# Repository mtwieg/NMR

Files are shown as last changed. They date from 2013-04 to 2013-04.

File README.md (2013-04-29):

NMR
===

Welcome to the Open Source Mobile NMR Relaxometry Platform repository on github.

You can download the entire repository without needing to install or register with github. To do so, go to the repository homepage and click the ZIP icon on the upper toolbar.

After presenting this project at ISMRM 2013, I received several questions about the future direction for the platform. At the moment there are numerous possible improvements to the hardware:

1. Further minitiarization (we estimate the platform could be shrunk by a factor of three or so without compromise).

2. Wider frequency range (for very low field work)

3. Addition of gradient amplifiers (imaging)

4. Greater processing power, for standalone data processing.

Such improvements should be driven by the intended applications of the platform, and at this time we have not settled on any applications to explore.  Until we decide what sort of applications are worth pursuing, we will probably hold off on any major hardware revisions.

We are, of course, open to any and all suggestions.

Mike Twieg
mdt24@case.edu

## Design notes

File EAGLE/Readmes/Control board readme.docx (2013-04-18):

Control board notes

The control board conditions the main DC supply voltage into the various supply rails for the rest of the platform. The main power input port is protected against reverse voltage polarity. There is also a resettable fuse and a clamp to protect against overvoltage (18V nominal) and prolonged overcurrent conditions. Operating the platform with supply voltages outside the nominal range (12-18VDC) will require modifications to the power chain.

The control board circuitry provides the option of shutting off different parts of the power supply chain to mitigate interference during signal acquisition. As of now, this feature has not been implemented, either in hardware or in firmware.

The control board has a 10 pin JTAG header which is used to program the MCU. For our purposes we used the JTAG ICE-3 programmer from Atmel in order to program and debug the platform firmware.

Some notes on uSD cards: Standard SD cards can operate in two modes: SD mode and SPI mode. Most electronic devices use SD mode; however, this requires a specialized peripheral interface from the host system, which was not available on our selection of MCU. Therefore we used SPI mode, which uses a simple SPI port found on most MCUs, including ours.

One implication of using the SD card in SPI mode is that the listed specifications for a given SD card are valid only for SD mode, and therefore performance in SPI mode is not guaranteed. We have discovered that in SPI mode, different card models and manufactures give vastly different performance results, independent of the label specifications. Certain SD card model (such as the SDSDQY-004G-A11A from SanDisk) performed quite well using SPI mode and our custom SD card firmware, and therefore we recommend using this model.

Michael Twieg

mdt24@case.edu

March 2013

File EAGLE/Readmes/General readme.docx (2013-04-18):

General schematic/layout

The circuit schematics and layouts were designed using Eagle Cad Professional. The free (hobbyist) version of Eagle should be able to display all included files, though editing them may not be possible without the Professional version.

The included BOMs cover all components except for basic, general purpose surface mount resistors and capacitors. Unless otherwise noted on the schematic, all resistors are 1% tolerance. General nonpolarized capacitors can be assumed to be NP0 dielectric for values of 1nF or less, and X7R dielectric for values over 1nF. All capacitors in case size 1008 are low loss NP0 types.

For professional PCB fabrication, we recommend either EIconnect or Advanced Circuits.

Michael Twieg

mdt24@case.edu

March 2013

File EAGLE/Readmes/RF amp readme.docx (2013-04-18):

Notes on the TRSW/RF amp circuitry

It has been observed that excessive RF power on the LNA input can lead to failure of the LNA. Adequate isolation on the RXSW is necessary to prevent this. See section 2-3 of the thesis for guidance on selecting Vr.

The gain control voltage of both VGAs can be set with potentiometers. The second stage VGA may also be set using the DAC from the MCU. When using the DAC for gain control, do not populate the potentiometer circuitry for the second stage VGA.

Michael Twieg

mdt24@case.edu

March 2013

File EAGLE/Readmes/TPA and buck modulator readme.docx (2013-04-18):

TPA and buck modulator notes

The buck modulator has the capability to deactivate its operation with the SHDN pin header. This feature has not been implemented yet, in either the firmware or hardware, as it was not deemed necessary.

Many component values in this design are specific to this TPA CMCD tuning (8.35MHz with a 1:4 balun). If the CMCD circuit is altered, changes to the buck modulator may also be necessary to preserve stability.

The LM5113 gate driver has shown to be useful at RF frequencies up to 20MHz. If higher frequency gate drive is desired, then it may be necessary to use a different gate drive circuit based on narrowband impedance matching circuits.

The tuning capacitors (C104 and C106) and the tank inductor (L1) for the CMCD were adjusted empirically to give good efficiency at the desired frequency. As a rule of thumb, the characteristic impedance of the resonant tank should be less than or equal to the load impedance looking into the balun.

Michael Twieg

mdt24@case.edu

March 2013

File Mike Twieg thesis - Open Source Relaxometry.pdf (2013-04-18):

OPEN SOURCE NMR RELAXOMETRY PLATFORM

by

MICHAEL TWIEG

Submitted in partial fulfillment of the requirements

For the degree of Master of Science

Thesis Adviser: Dr. Mark Griswold

Department of Electrical Engineering and Computer Science

CASE WESTERN RESERVE UNIVERSITY

January 2013

CASE WESTERN RESERVE UNIVERSITY

SCHOOL OF GRADUATE STUDIES

We hereby approve the thesis/dissertation of

Michael Twieg

Master of Science
candidate for the ________________________________degree *.

Mark Griswold
(signed)_______________________________________________ (chair of the committee)

Kenneth Loparo
________________________________________________

Francis Merat
________________________________________________

________________________________________________

________________________________________________

________________________________________________

July 23, 2012
(date) _______________________

*We also certify that written approval has been obtained for any proprietary material contained therein.

i

Table of Contents

ii

4-4: Example application: Measurement of G0 by diffusion weighted experiment.......98

4-5: Example application: Spoiling of milk | 100
4-6: Example application: Curing of adhesives | 102
4-7: Example application: Surface probe for biosensor applications | 107
Chapter 5: Conclusions and future directions | 109
Appendix A: Selected experiment parameters | 111
Appendix B: Circuit schematics | 120
Bibliography | 129

iii

List of tables

No tables

No tables

Table 4-4-1: Results of self diffusion coefficient measurement for three samples.....100

Table 4-7-1: Changing sensitivity and noise for the surface probe under different

iv

List of figures

Figure 1-3-2: Distortion of the FID due to B0 inhomogeneity results in an effective T2*

Figure 2-1-1: Schematic cross sectional diagram of our custom single sided magnet

Figure 2-1-5: a) Fit G0 vs. y using fitting window of 6mm b) Fit G0 vs. B0 using fitting

Figure 2-2-1: Cross sectional diagram of the magnet and harness with a flat surface coil

Figure 2-2-3: Cross sectional diagram of the magnet and harness with solenoid volume

Figure 2-2-5: Oscilloscope captures of the TXSW signal (channel 1, yellow) and the

Figure 2-3-2: Isolation between TX and RX ports when RXSW is on and TXSW is off

Figure 2-3-3: Isolation between TX and RX ports when RXSW is off and TXSW is on

Figure 2-3-4: Maximum permissible RF power isolated by the TRSW for two example

Figure 2-3-5: Attenuation from TX to Coil port when TXSW is on, RXSW is off.......39

v

Figure 2-3-6: Attenuation from Coil to RX port when TXSW is off, RXSW is on ......39

Figure 2-4-3: Spectral content of the 8.35MHz TPA output at full power (VD=12V),

Figure 2-4-4: Plots of drain efficiency and power added efficiency (PAE) vs.

Figure 2-5-2: Small signal step response of buck modulator between 6V and 8V........47

Figure 2-5-3: Large signal step response of buck modulator between 1V and 10V......47

Figure 2-6-2: Gain of the RF amplifier chain, with maximum gain for both AD8331

Figure 2-7-1: Frequency mixing of a real passband signal at f0 with a LO carrier........55

Figure 2-7-2: Simplified diagram of the downconversion stage, baseband amplifiers,

Figure 2-8-3: Block diagram of the power supply conditioning on the control board...64

Figure 3-1-1: CPMG readout sequence diagram, showing decay in spin echo amplitude

vi

Figure 3-1-5: Constant relaxation preparation sequence, with start of CPMG readout.74

Figure 3-1-6: Elimination of ringing artifacts from one spin echo via phase cycling ...75

Figure 3-2-1: Detailed operation of the platform I/O for synthesizing a RF pulse and
sampling a spin echo during a CPMG | 79
Figure 3-3-1: Hierarchy of the experiment structure | 82
Chapter 4: Hardware verification results | 89

Figure 4-1-1: a) Acquired data from a single spin echo. b) DFT magnitude of the
acquired echo, after zero padding to N=100 | 90

Figure 4-1-2: a) Acquired data from a single spin echo. b) Complex DFT of the
acquired echo, after zero padding to N=100 | 91

Figure 4-2-1: Results of flip angle calibration experiment for pulse width=10 μs and
pulse width=20 μs | 94

Figure 4-3-1: a) Measured echo amplitude for the above CPMG sequence. b)
exponential fit and error signal of the CPMG echoes | 97

Figure 4-4-1: a) Constant relaxation diffusion experiment results for a) DI water, b)
acetone, and c) glycerol | 99

Figure 4-5-1: Plots of experimental results for the fat free and whole milk samples
with different room-temperature storage times | 101
Figure 4-6-1: Photo of experimental setup for measuring curing of adhesives | 103

Figure 4-6-2: Plots of a) initial magnetization and b) apparent T2 for JBweld epoxy .104

Figure 4-6-3: Plots of a) initial magnetization and b) apparent T2 for exposed Duco
Cement | 105

Figure 4-6-4: Plots of a) initial magnetization and b) apparent T2 for Duco Cement in
between two fiberglass layers | 106
Chapter 5: Conclusions and future directions | 109

No figures

vii

Acknowledgements

First and foremost, I wish to give thanks to my research advisor Dr. Mark Griswold for his support and guidance throughout this project. Mark graciously introduced me into the incredible field of NMR/MRI, and gave me the opportunity to conduct research in one of the best imaging research groups in the country.

I am also indebted to Dr. Ken Loparo and Dr. Frank Merat for taking their own time to participate in my committee and review this work.

I also extend my warmest gratitude to the following:

To my many colleagues in the Case Center for Imaging Research, who provided me with support and advice on the theory and practice of NMR on countless occasions, and who shared their experiences and wisdom for my own benefit. They are Matt Riffe, Natalia Gudino, Lisa Bauer, Katie Wright, Dan Ma, Anagha Deshmane, Eric Pierre, Yun Jiang, Nahal Geshnizjani, Nicole Seiberlich, Greg Lee, and Vikas Gulani.

To Colin Blumenthal, the most diligent and reliable summer assistant I could possibly ask for.

To Carol Rice, for her swift handling of countless material requisitions.

To Cena Myers Hilliard, for her assistance in navigating the bureaucracy between our two departments.

To Joe Molter, for his assistance in the use of our 3D printer was invaluable throughout this project.

To Dr. James Basilion and Dr. Richard Agnes, for allowing me access to their lab equipment and materials on numerous occasions.

To Ed Burwell, George Daher, and Larry Sears, for affording me the incredible guidance and materials that turned me to electrical engineering.

To Beth Murray, for years of advice and tiny candies in EECS.

To Ian Charnas and the staff of the Thinkbox, for the use of various Thinkbox resources.

And last, but of course not least, to my parents Robert and Deborah for their unconditional love and support throughout my academic career.

viii

Open Source NMR Relaxometry Platform

Abstract

by

MICHAEL TWIEG

We present a low cost, open source hardware platform for use in NMR

relaxometry experiments. The platform is capable of a wide variety of relaxometry

experiments comprising many magnet, coil, and sample combinations. The majority of

the RF chain is broadband, allowing operation over a large frequency range with only

minor adjustments to the hardware. Experiments can be performed in a host-controlled

mode in conjunction with a PC, or in a standalone mode for mobile applications. The

high degree of flexibility and low cost of the platform makes NMR relaxometry

accessible to applications where cost, size, or flexibility were previously prohibitive. The

system is based on off-the-shelf components, along with some custom-fabricated parts,

and can be replicated by engineers with suitable skills and resources. The design of the

platform is open source.

Chapter 1: NMR relaxometry theory and applications

1-1 Content overview

Chapter one introduces the field of NMR relaxometry and its application. The

basic principles of NMR physics will be introduced, including magnetization, precession,

relaxation, and spin echoes. The Bloch equations and the effects of self diffusion will also

be derived. The influence of static field inhomogeneity and its impact on NMR

relaxometry will also be addressed. Finally, the field of NMR relaxometry and some of

its various applications will be discussed.

Chapter two describes the general hardware aspects of NMR systems. A

generalized NMR system will be divided into its basic components, and their roles within

the NMR system are discussed separately. We will show how the specifications for each

component are determined according to the specific requirements and limitations of the

application, and how we implement our hardware according to these specifications.

Finally, we will evaluate the performance of each component and its impact on the

overall system performance.

Chapter three covers the theory and implementation of NMR relaxometry

experiments on our platform. First we will discuss various pulse sequences and how they

can be used to obtain contrast according to various relaxation mechanisms. Secondly we

will explain how pulses are synthesized and how NMR signals are sampled with the

actual platform hardware, and how these events are combined into the desired sequences.

Thirdly, we will explore how the sequences are executed by the platform firmware, and

how sequences and experiments are defined within the firmware. Finally, we will discuss the user interfaces featured in the platform, and how data is stored and transferred within

the platform and between the platform and host.

Chapter four discusses the analysis of the overall platform performance and

experimental results. First we will discuss how sampled data from the platform is

analyzed using Fourier transforms and curve fitting algorithms. Secondly, we will explain

how sequence parameters can be calibrated for best performance. Thirdly, we compare

empirical measurements of signal to noise ratio and flip angle calibration with theoretical

predictions. Finally, we will demonstrate several examples of relaxometry experiments

and discuss their results.

Chapter five will provide an overview of the platform's specifications and

applications. Potential improvements to the platform hardware will be discussed. Finally,

we will speculate on future applications for the platform in research.

1-2 Introduction

Since its discovery, nuclear magnetic resonance (NMR) has shown to be an

excellent method of observing the nature and behavior of matter on the molecular scale.

While NMR was at first studied only within the fields of physics and chemistry, it has

since spread to a wide variety of disciplines and industries. Currently the most well

known application of NMR is medical magnetic resonance imaging (MRI), but it has also

found applications such as the investigation of molecular structures, porous media,

quality control for food products, inspection of polymer quality, and many more [2–10].

NMR is a particularly powerful tool because, given the correct magnet and coil

configuration, it can non-invasively penetrate into objects and provide spatial maps of many different material properties (which is the basis of MRI). Despite its power of

insight, it does not require any chemical reactions to occur and does not use any ionizing

radiation, and is thus a completely nondestructive method.

Arguably NMR's greatest weakness is the cost and complexity associated with the

various hardware components required to perform many studies. However, many simple

studies, especially those that do not require imaging, have much simpler requirements

that can be satisfied at lower cost. One subset of NMR studies with such low

requirements is NMR relaxometry. Despite its relative simplicity, NMR relaxometry can

provide valuable insight into many physical and chemical processes and structures.

The main motivation for the development of our relaxometry platform was to

make NMR relaxometry more accessible to researchers by lowering the cost and

complexity of the hardware, while still offering high performance and flexibility. The

platform allows for a wide variety of applications with various field strengths, magnet

and coil geometries, and samples. A secondary goal was to construct a system that was

small and portable, such that it could even be worn. As designed, the platform can be

used with its own battery, and it is small and light enough for mobile applications. The

platform is compatible with a large variety of different magnet and coil designers,

customized for the relaxometry application. However, the main magnet for such a system

is typically highly inhomogeneous, and requires specialized acquisition techniques to

ensure that the required signals are received with high sensitivity.

1-3 Fundamentals of NMR physics

Sample magnetization

The basis of NMR is that atomic particles possess a net spin, characterized by the

spin quantum number (s in the context of electrons, I in the context of nucleons). The

spin quantum number is quantized, and has allowed values of positive integers and half

integers. We will restrict our discussion to protons (in the form of hydrogen 1H), and

therefore use I as the spin quantum number, which has a value of ½. The secondary spin

quantum number mI describes the magnitude and direction of the angular momentum of

the nuclear spin, and can have values from –I to +I in integer steps. The spin of the

particle gives rise to a magnetic moment μ, which is given by:

- mI µ = γ
Equation 1-3-1

Where γ is the gyromagnetic ratio of the nucleus (

γ = 267.5rad s

for 1H) and ℏ is the

reduced Planck’s constant. For nuclei with no orbital angular momentum (such as 1H),

this can also be written as:

µ = γ I

Equation 1-3-2

Where

I
is the spin angular momentum vector. In the absence of an external magnetic

field, the different spin states described by mI are degenerate, meaning that all states

occupy the same energy level. At thermal equilibrium the members of a population of

nuclei will have their states evenly distributed, and the net mI
, and the net magnetization

of the population, will be zero [11].

If an external, static magnetic field

B0
is introduced to the population of nuclei,

the different states mI will no longer have the same energy level, and thus the population of spins will be biased parallel to

B0
. The spins will effectively polarize themselves to

align with

B0
, giving rise to a net equilibrium magnetization

M 0
[12]:

( )
kT
B M | N | I I
3

1

0

2 2
0
= γ +
Equation 1-3-3

Where N is the number of spins per unit volume, I is the nuclear spin quantum number

(I=
2

1
for 1H), k is Boltzmann's constant, and T is temperature.

The coordinate system describing a NMR experiment is typically defined such

that

B0
is aligned with the
z

ˆ
direction. Therefore from here on the static field

B0
will be

referred to simply as B0, and it will be assumed that it is in the z

ˆ
direction.

Larmor precession

When a macroscopic magnetization exists, the basic theory of nuclear precession

can be adequately described with classical, rather than quantum mechanics. A magnetic

moment
µ

will experience a torque

Γ
in the presence of an external magnetic field B

:

Γ = µ ×B
Equation 1-3-4

The torque results in a change in the angular momentum vector I

ˆ
:

= Γ
dt

d I
Equation 1-3-5

Combining equations 1-3-2, 1-3-4, and 1-3-5 yields the following:

B
dt

d
= γ µ ×

µ
Equation 1-3-6

Equation 1-3-6 states that when a nuclear moment µ

and

B
are not aligned,
µ

will rotate

around

B
with a frequency equal to ω [11]:

ω = γB
Equation 1-3-7

This phenomenon is called precession, and ω is known as the precession angular

frequency. We may rewrite equation 1-3-6 by splitting
µ

and

B
into their longitudinal

and complex transverse components:

z z µ = µ ·

ˆ

Equation 1-3-8

(x iy) xy µ = µ ·
ˆ
+

ˆ

Equation 1-3-9

B B z z
= ·

ˆ

Equation 1-3-10

B B (x iy) xy
= ·

ˆ
+

ˆ

Equation 1-3-11

( )

## [ (t)B (t) (t)B (t)]

i
dt
d | t
xy | xy | xy | xy

z

* | *
2
µ | µ
µ | γ
= | - | Equation 1-3-12

( )

## i [ (t)B (t) (t)B (t)]

dt

d | t
xy | z | z | xy
xy | γ µ | µ

µ
= - | - | Equation 1-3-13

If we consider the case where

B
is static with magnitude B0 and is aligned with the z

ˆ

direction, we find that equations 1-3-12 and 1-3-13 reduce to:

( )
= 0
dt

d t µ z
Equation 1-3-14

( )
( )B0
i t
dt

d t

xy

xy | γµ

µ
= - | Equation 1-3-15

Which have the solutions:

( ) | (0) z | z µ t = µ
Equation 1-3-16
( ) | | ( )
i | t
xy | xy t | e
0 0

ω
µ µ
=
Equation 1-3-17

Where

0 B0 ω = γ
is the Larmor precession frequency [11].

These equations are valid in the laboratory reference frame, which is stationary.

However, a more convenient way of describing NMR magnetization is with the rotating reference frame, in which the coordinate system rotates in the transverse plane at an

angular frequency Ω, which is normally set to be equal to ω0. Coordinates and variables

in the rotating reference frame are denoted with ' (for example
x

ˆ′ , B1

′ , µ xy
′
, etc). For the

case where Ω= ω0, equations 1-3-12 and 1-3-13 become:

( )

## [ (t)B (t) (t)B (t)]

i
dt
d | t
xy | xy | xy | xy
z | =
′ | ′ | - ′ | ′
| * | *
2
µ | | µ
µ | γ
Equation 1-3-18

( )
i (t)B (t)
dt
d | t
z | xy
xy | =
′

′
γµ

µ
Equation 1-3-19

And for our case of simple Larmor precession, equations 1-3-16 and 1-3-17 reduce to:

( ) | (0) z | z µ t = µ
Equation 1-3-20
( ) | (0) xy | xy µ′ t = µ′
Equation 1-3-21

We can see that the Larmor precession component of the transverse magnetization has

disappeared from the equations [11]. The transverse magnetization is still precessing in

the laboratory frame, but is stationary in the rotating reference frame.

Excitation via an RF magnetic field

Now we will consider the case where, in addition to the static field B0, we

introduce a circularly polarized magnetic field in the transverse plane with magnitude B1.

( )
i | t
xy B t | | B e
0
| | 1
- ω
=
Equation 1-3-22

When expressed in the rotating reference frame, B1 is constant and points in the x

ˆ′

direction:

( ) B1 B t
xy

′
=
Equation 1-3-23

The differential equations 1-3-18 and 1-3-19 then become:

( ) | B [ (t) | (t)]
i
dt
d | t
xy | xy

z

*
1 2
µ | µ
µ | γ
=

′ - ′
Equation 1-3-24
( ) | B1 dt
d | t

y

z | γµ

µ
=

′
Equation 1-3-25

( )
( )B1
i t
dt

d t

z

xy | γµ

µ
=

′
Equation 1-3-26

We can see that these equations describe rotation of the magnetization around the x

ˆ′

direction in the rotating frame. The rate of this precession ω1 is given by

1 B1 ω = γ
[11].

This precession describes how RF fields are able to manipulate magnetization, for

example by tipping it from the longitudinal axis
z

ˆ
into the transverse plane. RF fields are

needed to perturb the equilibrium longitudinal magnetization into the transverse plane in

order for precession to be detected.

An RF pulse is primarily characterized by its flip angle, which describes the

overall rotation of
µ

about

B1

. For example, a RF pulse with a flip angle of 90° may

rotate longitudinal magnetization completely into the transverse plane, and a 180° pulse

may invert longitudinal magnetization into the - z

ˆ
direction.

NMR relaxation and the Bloch equations

The previous equations describing Larmor precession are valid for an idealized

magnetic moment
µ

. However, in real NMR experiments we consider the overall

magnetization

M
from a sample, which is composed of the contributions of many spins

each with their own
µ

[11]. Large populations of spins undergo relaxation processes that

do not occur for isolated spins.

Longitudinal relaxation, also called spin-lattice relaxation or T1 relaxation, is the

process by which the longitudinal component of
M
approaches its thermal equilibrium value M0 (see equation 1-3-3). Longitudinal magnetization obeys the following linear

differential equation:
( ) | ( )

1

0
T

M M t
dt
dM t | z z
=
Equation 1-3-27

So longitudinal relaxation takes the form of an exponential decay towards M0 with a time

constant equal to T1 [11].

Transverse relaxation, also called spin-spin relaxation or T2 relaxation, is the

process by which the transverse component of
M
approaches zero. Transverse relaxation

obeys the following linear differential equation:
( ) | ( )

T2

M t
dt
dMxy t | - | xy
=
Equation 1-3-28

So transverse relaxation takes the form of an exponential decay towards zero with a time

constant equal to T2 [11].

Relaxation can be integrated into the previous equations in the following way:

( )
[ ( ) ( ) | | ( ) ( )]

( )

1

* | * | 0
2 | T
M | M t
M t B t | M t B t

i
dt
dM t | z
xy | xy | xy | xy

z

=
′ | ′ | - | ′ | ′ | +

γ
Equation 1-3-29

( )
( ) ( )

( )

T2

M t
i M t B t
dt
d | t | xy
z | xy

xy

′
=

′ -

′
γ

µ
Equation 1-3-30

These are the fundamental Bloch equations in the rotating reference frame, simplified for

on-resonance magnetization. Equation 1-3-31 below shows the correct equation for

M xy

′

when off resonance is considered:

( )
( ) ( ) | ( )

( )

T2

M t
i M t B t | i | M t
dt
dM t | xy
z | xy | xy

xy

′
=
′ | - Δ | ′ | -

′
γ | ω
Equation 1-3-31

Where Δω is the off resonance frequency [11].

The earliest NMR experiments were performed with continuous RF excitation,

while continuous absorption [13] or emission [14] of energy due to Larmor precession

was observed. Later on, experiments used pulsed RF to quickly tip, or excite, longitudinal

magnetization into the transverse plane, and it was found that precession persisted long

after the end of the RF pulse itself. The precession which persists after an excitation pulse

is referred to as free induction decay, or FID [15].

Suppose that the static field B0 is perfectly homogeneous (Δω and ΔBz are zero),

and that the sample magnetization has reached its thermal equilibrium (

M | M z ˆ
0 = | ·
). If

we apply a 90° excitation, then all of Mz will be tipped into the transverse plane where it

precesses as a FID. The FID will decay according to T2, and Mz will relax from zero back

towards M0 according to T1.

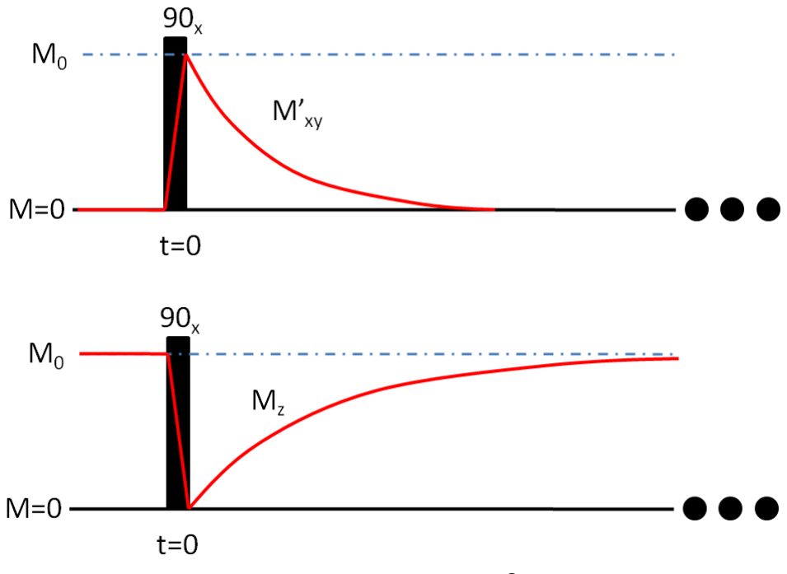
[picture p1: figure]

Figure 1-3-1) Diagrams of a simple FID experiment. At

t < 0
, Mz has reached the thermal equilibrium value M0, and Mxy is 0. At

t = 0
, a 90° RF pulse in the

x

ˆ′
direction tips all of Mz

into M'xy. a) shows the
decay of M'xy (solid red line) according to T2 b) shows the regrowth of Mz (solid red line) towards M0 (dashed blue line) according to T1.

Transverse relaxation and longitudinal relaxation are relevant because they provide a

macroscopic fingerprint of microscopic phenomenon in the environment of the spins. The

exact mechanisms of this relaxation are beyond the scope of this work, but there are countless examples of prior studies that confirm that NMR relaxation can provide key

insight into the environment of a material at a molecular scale.

B0 inhomogeneity and T2*

In the case where the static field is not perfectly homogeneous within the volume

of a sample under test (SUT), the macroscopic behavior of the transverse magnetization

will differ from the ideal FID. This is because any field inhomogeneity will result in a

frequency inhomogeneity, which will contribute to dephasing of the spins within the

SUT. This results in an apparent change to the shape of the overall FID. The exact shape

of the FID will depend on the exact nature of the inhomogeneity, but the overall result is

that the FID will decay at a rate faster than its spin-spin relaxation rate T2. The new

inhomogeneity-weighted decay time constant is referred to as T2* (even though this does

not necessarily obey a purely exponential decay [11]).

Figure 1-3-2) Distortion of the FID due to B0 inhomogeneity results in an effective T2* which is less than T2. The shape of this FID will depend on the specific nature of the inhomogeneity, and may not be exponential. The dashed red line shows a hypothetical FID in a homogeneous field, while the solid red line shows the FID in the presence of field inhomogeneity.

In many cases, inhomogeneity is so severe that T2* is far less than T2, making

observation of T2 impossible from a simple FID experiment. In such cases, spin echoes

must be used to rephase the magnetization.

Spin echoes

The Hahn echo (sometimes referred to simply as a spin echo) is a technique used

to observe the FID in the presence of B0 inhomogeneities, and was originally described

by Erwin Hahn [16]. In a simple Hahn echo experiment, an excitation pulse in the
x

ˆ′

direction occurring at
t = 0

tips some or all of Mz into the transverse plane (initially in

the
y

ˆ′
direction). The transverse magnetization is allowed to precess and decay according

to T2*. At some time
t =τ

, there is another RF pulse with a tip angle of 180° (again in

the
x

ˆ′
direction), called a refocusing pulse. The refocusing pulse rotates the magnetic

moment
µ

of each spin around the
x

′
axis, such that their transverse moments become:
( ) | ( )
+ | -
µ′ τ = µ′ τ
| *
xy | xy

Equation 1-3-32

This can also be viewed as a phase reversal of each spin:
( ) | ( )
+ | -
θ τ = -θ τ
Equation 1-3-33

After the refocusing pulse, each spin will continue to precess at its own off resonant

frequency and in the same direction, but now instead of the phase of each spin continuing

to diverge from zero, it will converge towards zero at the same rate. The result is that at

time
t = 2τ

, the phase of all spins will again be zero, and they will be coherent until they

again dephase. Aside from the Hahn echo, there are various other spin echo types that

rephase magnetization in their own way. However for the scope of this work, only Hahn

echoes will be considered.

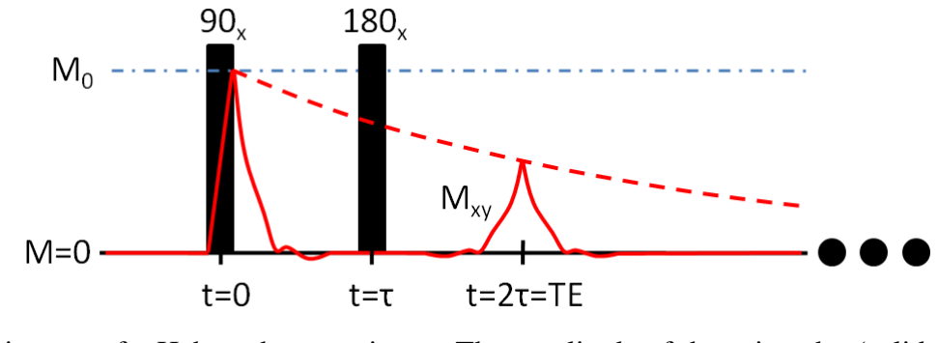
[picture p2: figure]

Figure 1-3-3) Diagram of a Hahn echo experiment. The amplitude of the spin echo (solid red line) at t=TE will be the same as the amplitude of the ideal FID without inhomogeneity (dashed red line).

Though the spin echo restores coherency in the spins at time
t = 2τ

(also called

the echo time TE), transverse relaxation still occurs due to spin-spin relaxation during

that time, and that loss in transverse magnetization cannot be restored by the refocusing

pulse (because it is due to random processes which cannot be reversed). Thus the peak

amplitude of the spin echo will still be weighted by T2 decay. This allows T2 weighted

experiments to be performed even in the presence of strong inhomogeneity in B0.

Self-diffusion

In a spin echo experiment performed in an inhomogeneous field, the amplitude of

the spin echo at the echo time TE will be equal to the initial magnetization, attenuated by

T2 relaxation. This is the case when the Larmor precession frequency (and therefore Δω)

of each spin remains constant throughout the experiment. If this is not the case, either due

to motion of the nuclei or changes in ΔB0 during the experiment, the time of the echo

coherence, or the amplitude of the echo, may be altered. One particularly relevant

example of this is molecular self-diffusion.

Self-diffusion is the phenomenon that describes the Brownian motion of particles

in a medium when the overall chemical gradient is equal to zero. The self-diffusion

coefficient D of some particles in a medium describes the mean square spatial deviation

2
δ
of the spins per unit time
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
Equation 1-3-34

Suppose the strength of our static field B0 is not constant over space, and instead varies

linearly in one arbitrary direction
g

ˆ
such that its
z

ˆ
component Bz as a function of

position
r
is given by:

Bz

## (r) Bz

(0) G r g
ˆ
0 = | + | ·
Equation 1-3-35

This is commonly referred to as a field gradient, where G0 is called the gradient strength,

in Teslas per meter. It can be found that if a population of spins is allowed to self diffuse

with D in a linear gradient G0 for time t, the spins will evolve with a random distribution

of phase [11]:

2 2 3
0

2 3
ˆ

2 2
2 | 0
3

2
3
G | Dt
G | t

d

r
γ
τ

γ δ
φ = | =

Equation 1-3-36

This dephasing causes a loss in overall transverse magnetization (ignoring the effects of

T2) according to [11]:

( ) ( )
2

2
0

φ
M | t = M | e xy | xy

Equation 1-3-37

( ) ( )

G t D
xy | xy M t | M | e

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
Equation 1-3-38

This decay is often much faster than T2 decay, especially in viscous liquids and strong

gradients. However, the effect of self-diffusion on the magnetization can be mitigated

through the use of spin echoes. Consider a simple Hahn echo experiment as described

previously. During the interval

0 < t <τ , the magnetization will relax according to

equation 1-3-38 above. At

t =τ
:

15 ( ) | ( )
G | D
xy | xy M | M | e

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
Equation 1-3-39

At
t =τ

the refocusing pulse reverses the phase of each spin. Starting from

+
t =τ
, the

magnetization continues to dephase from

( )
+
τ M xy
according to equation 1-3-38, and at

t = 2τ

, a spin echo will occur with:

( ) | ( )
G | D
xy | xy M | M | e

2 3
0

2
3

1
2
γ | τ
τ | τ
- +
=
Equation 1-3-40

Substituting equation 1-3-39 into equation 1-3-40 yields:

( ) | ( )
G | D
xy | xy M | M | e

2 3
0

2
3

2
2 | 0
γ | τ
τ
=
Equation 1-3-41

Contrast this with the magnetization of a free induction decay experiment with no

refocusing pulse after the same period time 2τ:

( ) | ( )
G | D
xy | xy M | M | e

2 3
0

2
3

8
2 | 0
γ | τ
τ
=
Equation 1-3-42

And it is seen that the contribution from self-diffusion to transverse decay is decreased by

a factor of four. This suppression of diffusion effects by using spin echoes is called the

Carr-Purcell mechanism [17].

If we factor spin-spin relaxation back into equation 1-3-40, then the spin echo

amplitude will be:

( ) ( )
2

2 3
0
2 | 2
3

2
2 | 0
G | D | T
xy | xy M | M | e | e

τ
γ τ
τ
=

Equation 1-3-43

Substituting t for 2τ yields the function of the echo amplitude vs. time:

( ) ( )
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
t G | Dt
xy | xy M | t | M | e | e
=

γ τ
Equation 1-3-44

Which can be rewritten as:

( ) ( )
T a

t
xy | xy M | t | M | e
2 0
=

Equation 1-3-45

Where T2a is the apparent transverse relaxation time constant given by [11]:

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
= | +
T

T a

γ G τ D
Equation 1-3-46

We can see from equation 1-3-46 that the effective relaxation time of a population of

spins is weighted by many factors, including the sample’s intrinsic T2, self diffusion

coefficient D, the gradient strength G0, and the TE (where

TE = 2τ
) of the Hahn echo

sequence. As the quantity

G D

2 2
0

2
3

1 γ τ
decreases such that

2

2 2
0
2 | 1
3

1
T

γ G τ D <<
, T2a

will approach the sample’s intrinsic T2.

In practice, it is possible to refocus the magnetization multiple times and generate

multiple spin echoes in order to further suppress the effects of self diffusion and

inhomogeneity on transverse relaxation. The CP and CPMG techniques are examples of

such sequences wherein many spin echoes are generated from one excitation pulse. The

CPMG experiment is described in more detail in chapter 3.

Spatial frequency encoding in static gradients

Since this work is directed at NMR experiments in which there is a strong static

field inhomogeneity, the effects of this gradient on signal evolution must be considered.

Consider a sample of nuclei with some thickness l in the
y

ˆ
direction and is centered at

y = 0

. The sample is in the presence of a static magnetic field B0 in the z

ˆ
direction with

a gradient G0 in the
y

ˆ
direction:
B y | B ( ) G y 0 | 0 0 | 0
( ) = | +
Equation 1-3-47

Now suppose we wish to apply an RF pulse that tips the entire sample into the transverse

plane. All the spins must be excited at their Larmor frequency, but the sample has a

distribution of Larmor frequencies in the
y

ˆ
direction, and thus an associated bandwidth

[11].

f | G y | G l 0 | 0 Δ = γ Δ = γ
Equation 1-3-48

To excite the entire volume, the RF pulse must have an effective tip angle of 90°

over the bandwidth

f G l
0 Δ = γ

. If the bandwidth of the pulse is such that Δy is less than l,

then only the portion of the sample with Larmor frequencies within that bandwidth will

be excited. This effect is often exploited in both NMR and MRI to selectively excite

specific volumes of interest while rejecting contributions from other regions.

It is often desired for a RF pulse to have a uniform flip angle within some

bandwidth and volume of interest, and a flip angle of zero everywhere else. However,

practical limitations on the hardware and sequence parameters require that this condition

not be perfectly met. Real pulses will have a distribution of flip angles as a function of

frequency (and therefore space). As will be explored later, this can potentially cause the

observed magnetization to differ from what is predicted by ideal RF pulses.

Similarly to how the application of a static gradient field allows for volume

selection by controlling the bandwidth of the RF pulses, the NMR signal itself will be

given spatial-frequency encoding. Consider a sample whose magnetization varies in the

y

ˆ
direction according to some function Mxy(y). In the presence of a static gradient G0,

also in the
y

ˆ
direction, the magnetization from the sample at location y will precess in

the rotating reference frame according to (neglecting all relaxation effects):

18 ( ) ( )
i G yt
xy | xy M | y t | M | y e
0
, | ,0
- γ
′
=

′
Equation 1-3-49

The overall magnetization of the sample can be derived by integrating this contribution

over the entire span of the sample in the
y

ˆ
direction:

( ) ( )

ò
- M′ t = M′
y e | dy i G yt
xy | xy

0

γ
Equation 1-3-50

The form of this equation is the Fourier transform, and thus the time-domain

magnetization detected from all the spins is the Fourier transform of the spatial

magnetization in the
y

ˆ
direction [11]. This phenomenon is the basis of magnetic

resonance imaging (MRI).

This work does not deal with the topic of imaging, but the effects of a gradient on

the frequency content of the NMR signal are still relevant. For applications with a high

G0, the thickness l of the sample will generally be much greater than the thickness of the

slice Δy selected by the RF pulses. Therefore the slice thickness of the magnetization

excited by the RF pulses will be determined by the bandwidth of the RF pulses:

G0

f
y
γ

Δ
Δ =
Equation 1-3-51

And since G0 is constant throughout the experiment, the echo bandwidth will be equal to:

Δf = G Δy 0
γ
Equation 1-3-52

And thus when the gradient strength and direction is constant throughout an experiment,

the bandwidth of the spin echoes will tend to have the same bandwidth as the RF pulses

(neglecting factors such as relaxation, flip angle inhomogeneity, etc).

1-4 NMR relaxometry

NMR relaxometry is the observation of chemical and physical properties and

processes in a SUT through the measurement of apparent relaxation rates. The principle

contrast mechanisms in NMR relaxometry experiments are T1, T2, and D. NMR

relaxometry is convenient because these contrast mechanisms do not have strict

requirements for the strength or spatial homogeneity of B0 and B1, which are often

responsible for the high cost of NMR systems. In addition, relaxometry experiments do

not necessarily require a gradient system. T1 and T2 can be observed in the absence of any

gradients, while diffusion effects do require some gradient. However, for diffusion

effects, the strength or direction of the gradient does not need to be controlled, and can

merely be static (though control over gradients allows for more degrees of freedom in the

experiment). Static gradients can easily be generated by the fringe field of any type of

magnet.

The relatively simple requirements of NMR relaxometry systems make them

appealing for applications where factors such as low cost and small size are important.

Here we list a few example applications found in literature and industry that are be

compatible with the capabilities of our relaxometry platform.

Self diffusion coefficient measurement

NMR relaxometry is by far the most common method of measuring the self

diffusion coefficient of liquids. Many studies of the measurement of D using single sided

NMR probes with static gradients have been published, and show good accuracy despite

the simplicity of the hardware involved [7], [18]. In addition to measurements performed on simple liquid samples, Flaum [6] and Rata et al [7] have shown the use of single-sided

NMR relaxometry in studies of restricted self diffusion in porous media.

Solid state NMR material characterization

Single sided NMR relaxometry has gained acceptance as a method for

investigating the structure of solid samples, especially in polymers. Single sided NMR

systems are especially suited to solid state media because their strong static gradients

allow for very high bandwidth operation and thus very short echo times, enabling them to

resolve very fast relaxation processes seen in solids.

Various studies have demonstrated that there is a close correlation between

crosslinking density in polymers and transverse relaxation time. Blümich et al and Goga

have shown that such dependencies are easily detectable with single sided relaxometry

[2], [10]. Their studies show the use of NMR relaxometry in detecting the degree of

vulcanization in tire rubber, damage and stress in PVC piping, and the curing of polymer

adhesives.

Perlo et al has also shown the use of a single sided system for one dimensional

stray field imaging (STRAFI). This type of imaging technique does not rely on

controllable gradients, but instead relies on displacement of the SUT in the direction of

the static gradient in order to form a one dimensional profile of the SUT's NMR

properties [19]. Therefore this application is suitable for our platform.

Quality control in edible products

NMR relaxometry has also found niche roles in quality control for edible

products. The bakery, confectionary, and margarine industries have accepted NMR

relaxometry as a standard means of measuring solid fat content in raw ingredients [4],

[20]. NMR relaxometry has also become a standard method of measuring moisture and

oil content in oil-bearing crops [9]. Guthausen et al have shown the use of a NMR

MOUSE for the measurement of fat content in various foods without removing them

from their packaging [8]. Stork et al have demonstrated the use of a "semi-single-sided"

magnet array for detecting oxygen content in commercial table water [5]. All of these

applications are compatible with the capabilities of our relaxometry platform.

Throughout the course of this work, we will demonstrate that the platform is

capable of performing similar experiments to those listed above. In addition, we will

show that the platform has a degree of versatility and mobility not yet seen in any NMR

system. We hope that this will allow for new avenues of research into mobile and

wearable applications, especially for biomedical applications.

Chapter 2: Hardware design and verification

In this chapter we will discuss the role of various components of the NMR

platform, and how their characteristics were specified according to the desired

applications. We will also discuss the implementation of the hardware, and

measurements of the performance of each component.

2-1 The Magnet

The properties of the NMR magnet define many of the capabilities and limitations

of an NMR system. The strength of the magnetic field B0 within the volume of interest

(and the nuclei of interest) determines the system's Larmor frequency f0. The equilibrium

magnetization M0 of the sample will also be proportional to B0. The spatial profile of the

field within the volume of interest also determines what experiments and applications are

feasible with the magnet. Applications such as imaging (MRI) and spectroscopy typically

require very homogeneous B0, while other simple NMR experiments, such as

measurement of relaxation and diffusion in bulk samples, do not.

The physical shape and size of the magnet and its B0 will also determine its

suitability for various applications. Closed magnets, in which the volume of interest is

surrounded by the magnet, can generally achieve higher field strengths and more

homogeneous B0 than open/single sided magnets, where the volume of interest is

completely outside of the magnet. However, closed magnets are limited to subjects that

fit inside the magnet's volume, while single sided magnets may be used with objects

much larger than the magnet itself.

There are three major magnet varieties that are useful for creating NMR/MRI

systems. Permanent magnets generate a static field which requires no electronics, are

relatively inexpensive, and can have moderate field strengths up to 1T. However,

permanent magnets often suffer temperature drift and manufacturing variance, and are

thus not suitable for applications requiring a stable and homogeneous B0. Resistive

electromagnets use conventional current carrying conductors to create a magnetic field.

These systems can generate strong and homogeneous fields, but require large amounts of

power and cooling due to the magnet's resistance. Superconducting electromagnets are

the highest performing magnet type, since they can generate a very strong and

homogeneous B0 while effectively dissipating no power. However they require

sophisticated cooling systems and construction to maintain a superconducting state,

making superconducting magnets very expensive.

For this work, we chose to create a single sided magnet array comprised of

permanent rare earth magnets. There are a wide variety of published permanent magnet

designs, but all exhibit a relatively strong static gradient G0 relative to B0. A strong G0 is

useful for high resolution 1-D imaging (STRAFI) [7], and for diffusion measurement of

high viscosity samples. However, a high G0 results in a narrower slice thickness for a

given bandwidth, and thus a smaller volume of sample that can be analyzed, and lower

SNR per equivalent bandwidth. Also, measurement of T2 is difficult in low viscosity

samples due to the heavy effective weighting of self-diffusion on transverse relaxation.

Because of these factors, we chose to design a novel magnet array with a

significantly lower gradient, while still maintaining acceptable B0, homogeneity, weight,

and penetration depth. A simple cross sectional diagram of the magnet array is shown below. B0 is primarily in the z

ˆ
direction, while G0 is in the y direction. The length of the

magnets (in the

x

ˆ
direction) is two inches. We initially targeted a penetration depth of

y=7 mm from the magnet surface, on the basis that it would be deep enough for in-vivo

biosensor applications, while providing an adequate compromise in sensitivity.

Figure 2-1-1) Schematic cross sectional diagram of our custom single sided magnet array, showing the coordinate system used. Black arrows indicate the polarization of the permanent magnets, and dashed lines show the static field B0.

The magnetic field of the magnet array was simulated with Finite Element

Method Magnetics (FEMM) 4.2, a simple free 2D Finite Element Method program [21].

At a distance of 7 mm from the top surface of the center magnet, the field strength at z=0

and x=0 was predicted to be 235.9 mT, and the gradient in the y direction was 7.01 T/m

(averaged between y=6 mm and y=8 mm).

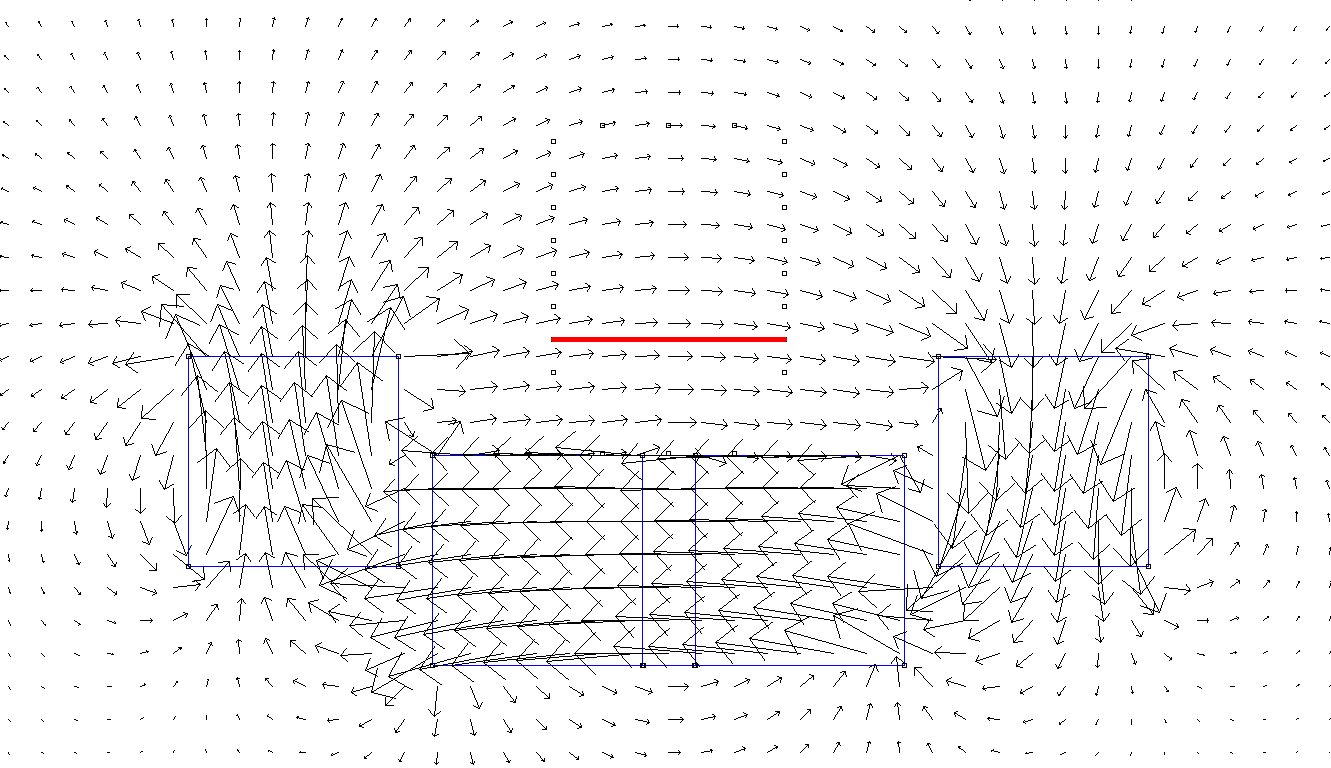
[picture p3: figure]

Figure 2-1-2) Simulated vector plot of our custom surface magnet array. The red line shows the intended sensitive volume at y=7 mm.

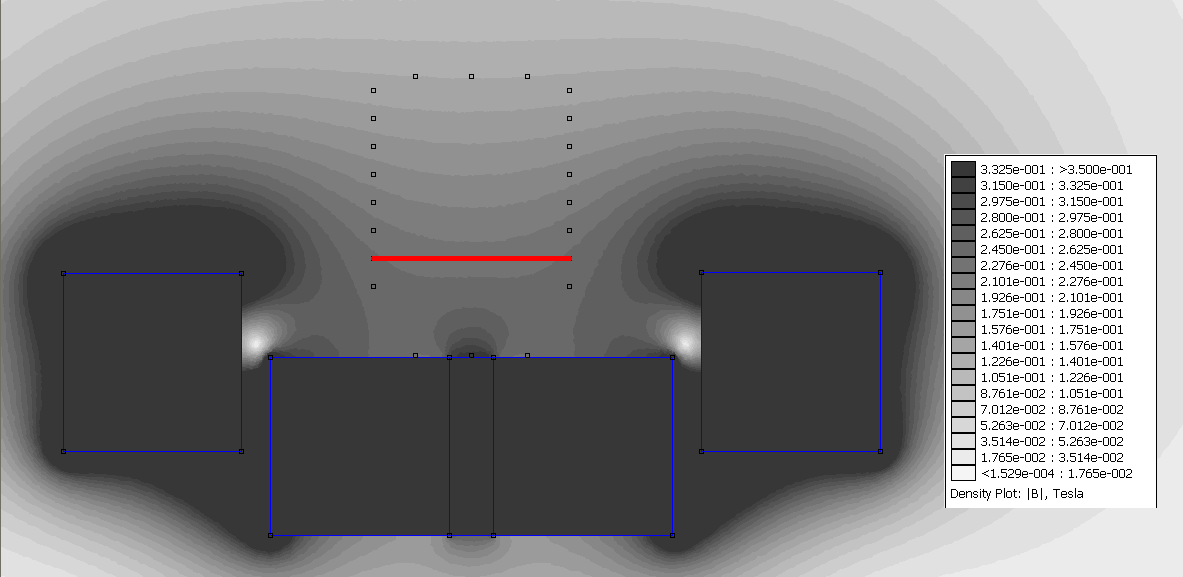
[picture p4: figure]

Figure 2-1-3) Simulated field density plot of our custom surface magnet array. The red line shows the intended sensitive volume at y=7 mm.

The magnet was constructed using permanent magnets obtained from Applied

Magnets. The harness for the array was fabricated using a Projet SD 3000 3D printer

from 3D Systems Corporation. The array measures 70x64x24 mm and weighs

approximately 0.6 lbs without a coil mounted. After construction, the Bz of the array at

y=7 mm was roughly measured using a DTM-151 Teslameter from GMW Associates.

The measured B0 at this depth was approximately 196.1 mT, corresponding to a f0=8.35

MHz for protons. Based on this measurement, all subsequent experiments were

performed at 8.35 MHz.

An apparatus for mapping Bz in the y

ˆ
direction was constructed, allowing for

accurate and repeatable measurements of both B0 and G0 as a function of y. The

Teslameter probe was sensitive in the
z

ˆ
direction, and measurements of Bz and the actual

y were taken along the y-axis from y=3.4 mm to y=12.9 mm in steps of 0.5 mm. This

measurement was repeated in four passes. The four passes were averaged together to give

the data shown in figure 2-1-4 below:

Figure 2-1-4) Field measurements of the custom surface magnet vs. y. The y and Bz values of four passes

Though this curve appears very linear, its gradient varied significantly, and thus we

wanted to determine the spatial profile of G0. To determine the gradient at a given y, the

measurements within a small given window Δy were applied to a linear fit, and the slope

of this line was taken as the gradient, while the value of the line at y was taken as the true

value of Bz at y. The results are shown below for Δy=6 mm:

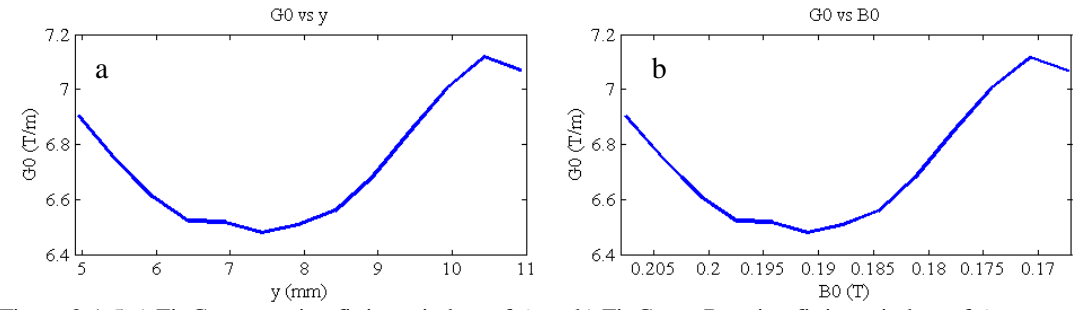
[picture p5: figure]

Figure 2-1-5 a) Fit G0 vs. y using fitting window of 6mm b) Fit G0 vs. B0 using fitting window of 6 mm.

These detailed measurements showed that our chosen frequency of 8.35 MHz actually

was located at y=6.65 mm, and the G0 at this field strength was 6.52 T/m. The difference

in these measurements and the simulated results was mostly due to the fact that the real

magnet is of finite length, while FEMM assumes infinite length in the

x

ˆ
direction.

Variation in the individual magnets' strength and errors in the harness's dimensions also

contribute to this disagreement.

Despite the lower than expected field strength, the magnet's G0/B0 ratio was

significantly lower than other single sided arrays of comparable weight and size, making

it suitable for mobile relaxometry experiments with good penetration depth.

2-2 The RF Coil

The purpose of the RF coils in an NMR system is to both manipulate and sense

the magnetization of the sample. An NMR system may contain separate sets of coils for

B1 transmission and signal reception, and often each is comprised of multiple coils in an

array. A single transmit/receive (TR) coil may also be used.

Coils are characterized by their ability to sense and transmit B fields with high

sensitivity and low losses and noise. One important coil parameter is B1 efficiency

(specified in Tesla per amp or Tesla per √W), which describes the relationship between

the current or power delivered to the coil with the B1 field it transmits or receives at a

certain location in space relative to the coil. Another specification of a coil is the quality

factor Q, which describes the ratio between the reactive and resistive impedance of the

coil at its operating frequency.

R

Q = X
Equation 2-2-1

For a transmitting coil, the power P required to generate a certain B1 will be inversely

proportional to its Q [12]:

Q

B ∝ P
1

Equation 2-2-2

For a receiving coil, the SNR of the received signal will be proportional to the square root

of Q (assuming the bandwidth of the received signal is less than the bandwidth of the

coil) [12]:

SNR ∝ Q
Equation 2-2-3

Also, the bandwidth of an impedance matched coil (assuming a simple matching network

tuned to one frequency) will be inversely proportional to Q:

Q

BW ∝ 1
Equation 2-2-4

While high Q is usually desirable, it may sometimes be necessary to decrease Q for

applications that require a wide bandwidth.

The physical shape and size of a RF coil will determine its electrical properties, as

well as which applications it is suited for. There are a vast variety of coil geometries in

use for NMR, but the scope of this work will confine itself to simple coil geometries

suitable for small systems. Volume coils, such as solenoid coils, can have relatively high

Q. Because the sample is inside the coil itself, it will also have a high B1 efficiency and

good homogeneity. While the high Q and B1 efficiency of volume coils often results in

good SNR, they are not suitable for applications where the dimensions of the coil are

restricted, or where the sample is much larger than the volume of interest. In such

applications, flat surface coils are often necessary. While surface coils generally have

lower Q than volume coils, their ability to excite specific volumes of interest in large

samples will often give better overall B1 efficiency and SNR, especially with shallow

penetration depths. However, surface coils usually suffer from poorer B1 homogeneity

than volume coils.

For surface sensor applications, the space allocated to the RF coils is severely

limited since the coils must occupy a space between the magnet surface and the sample.

Since the thickness of the coils effectively decreases the penetration depth of the overall

sensor, it was desirable to construct these coils to be as thin as possible. For this reason

we chose to use single T/R surface coils for single sided applications.

The RF surface coils used in this work were made from double sided or 4-layer

copper clad printed circuit board, which can be etched or milled for excellent precision

and repeatability. All measurements of the TR coils were performed using a E5061A

vector network analyzer (VNA) from Agilent.

Figure 2-2-1) Cross sectional diagram of the magnet and harness with a flat surface coil. Black dots show the location of coil conductors, and dashed lines show an example B1 field. The SUT is much larger than the probe itself, but only a small slice of it (shaded red) is excited by the coil.

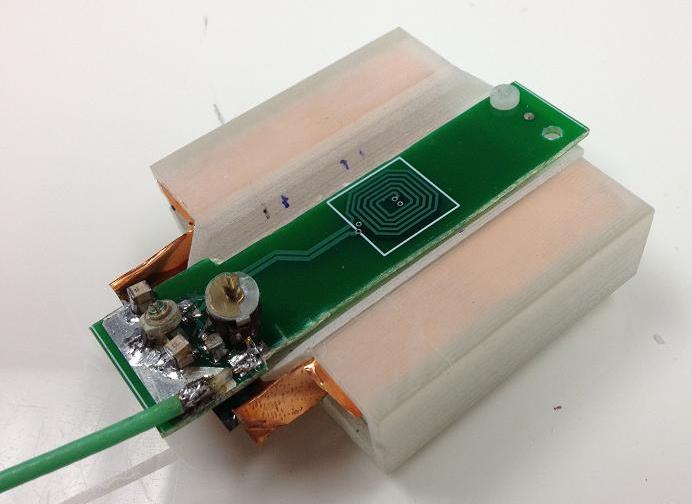
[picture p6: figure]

Figure 2-2-2) Photo of the surface magnet fitted with the spiral surface coil. The 50 Ω matching network is local to the coil, allowing it to be connected with common 50 Ω coaxial cable.

Coil impedance at 8.35 MHz (measured with VNA) | Z=3.877+j155.1 Ω
Coil outer radius | 7.15 mm
Coil inner radius | 4.2 mm
Coil thickness | 1.7 mm
Number of turns | N=20 of 1oz copper
Calculated B1 efficiency (simulated with FEMM) | 1.4 mT/A
Table 2-2-1) Properties of the spiral surface coil in figure 2-2-2. These properties are measured and simulated with the coil mounted on the magnet, with 1.7 mm of spacing between the magnet harness and the bottom of the coil. This is the configuration used for the measurement of drying adhesives in section 4-6.

We also used a simple solenoid volume coil with small liquid samples that did not

require a surface sensor. The solenoid coil's higher Q and B1 efficiency yielded a higher

SNR, and required less power for RF pulses.

Figure 2-2-3) Cross sectional diagram of the magnet and harness with solenoid volume coil. Black dots show the location of coil conductors, and dashed lines show an example B1 field. The SUT fits inside the coil, and only a small slice of it (shaded red) is excited.

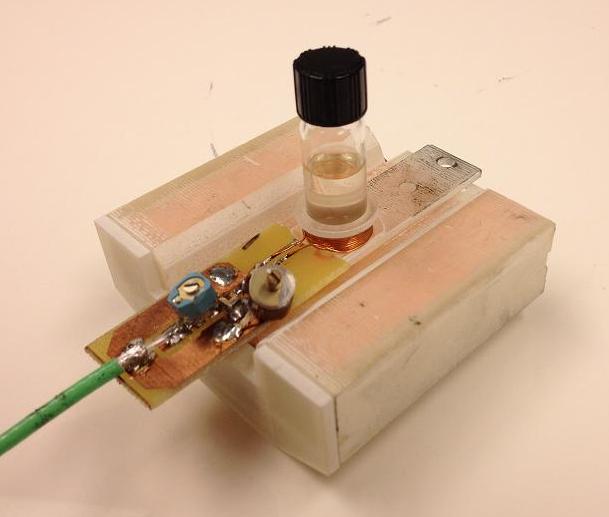
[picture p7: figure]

Figure 2-2-4) Photo of the surface magnet fitted with the solenoid volume coil. The coil was designed to hold small glass vials for the SUT. A SUT of canola oil is shown in the coil.

Coil impedance at 8.35 MHz (measured with VNA) | Z=0.95+j90.8 Ω
Coil radius | 6.7 mm
Inner radius of sample holder | 5.2 mm
Cross sectional area of vial volume | 2 77.8 mm
Coil height | 4 mm
Number of turns | N=11 of 28AWG wire
Calculated B1 efficiency [12] | 988 μT/A
Table 2-2-2) Properties of the solenoid volume coil in figure 2-2-4. These properties are measured and calculated with the coil mounted on the magnet such that the center of the coil lies 5.5 mm from the surface of the harness (y=7 mm). This is the configuration used for all experiments of liquid samples.

Coil integration and matching

For our platform, we desired the coil and magnet to not be directly integrated into

the platform hardware (as opposed to many spectroscopy systems that integrate the

magnet, coils, and other electronics in one enclosure). Thus the magnet and coils were

designed as separate components that can be combined at will, effectively making a

standalone NMR probe. A 50 Ω coil impedance matching network [22] was integrated

into the probe assembly so that it could be connected to with a simple 50 Ω coaxial cable.

The platform was also given a 50 Ω coil port (see section 2-3), allowing us to easily

switch between multiple probes, and also allowing the probe to be moved and positioned

independently of the platform hardware.

Magnet shielding and dead time

While a coil's operation may be predictable when operating in free space, it

suffers from some non-ideal behavior when placed inside the magnet's B0. The magnets

themselves are conductive, and thus the magnetic and electric fields from the RF coil will

induce currents in the magnets. These currents will result in additional Ohmic losses,

lowering the overall Q and B1 efficiency of the coil.

The strong RF fields and currents which occur during transmit pulses also give

rise to electromechanical disturbances in the system. All currents in the coil and magnet will produce Lorentz forces, causing vibration and "ringing" in both the coil and the

magnet itself, called magnetoacoustic ringing. Such motion can cause disturbances in B0,

and create interference in the received signal. These effects may persist for significant

periods of time (hundreds of microseconds) even after the end of a transmit pulse [23].

Though this usually has no noticeable impact on the coil's measured electrical

characteristics, it can be problematic in experiments that require fast recovery of the

detected signal after transmit pulses.

To address the problems caused by magnetoacoustic ringing, we put thin copper

sheets on the inner surface of the magnet, as suggested previously by Anferova et al [22].

The eddy currents caused by the RF coil circulate almost entirely in the copper sheets,

rather than the magnet, which shields the magnet from the magnetic and electric fields

from the coil. The copper may still vibrate due to Lorentz forces, but the vibration in the

magnets is greatly reduced, resulting in less disturbance to B0.

The construction of the RF coil also has significant impacts on its dead time. In

agreement with these previous publications [22], [23], we observed that surface coils

made from etched PCBs had much less ringing than solenoid coils made from wound

magnet wire. This was likely due to the conductors in etched coils being much more

rigidly fixed than the windings of wound coils. Also being shorter in the direction of G0

meant that surface coils were subject to less net force between the top and bottom of the

coil, thus reducing the net force between the coil windings.

By applying the copper shield to the surface magnet and using an etched surface

coil, we were able to reduce the dead time of the system to under 25 μs. We define the

dead time measurement by the amount of time after the end of the transmit pulse that the disturbances in the baseband signal drop below the noise floor. Figure 2-2-5 shows the

benefit of magnet shielding in reducing artifacts due to magnetoacoustic ringing.

Figure 2-2-5) Oscilloscope captures of the TXSW signal (channel 1, yellow) and the in-phase baseband signal (channel 2, green) after a RF pulse. Acquired when using a solenoid volume coil. a) Without copper shielding on the magnets, very large magnetoacoustic ringing is observed, and persists above the noise floor for nearly a millisecond. b) After adding copper shielding, magnetoacoustic ringing is damped below the noise floor within 21 μs after the end of the RF pulse. Data is captured with trace averaging (N=16).

Probe shielding

Due to the low signal powers typical of single sided NMR experiments, the NMR

probe (comprised of the magnet and RF coil) is very susceptible to interference from

external fields. Special care must be taken to ensure that such interference does not

contaminate the NMR signal. For this reason, we perform most of our experiments with

the probe inside a shielded enclosure. The 50 Ω cable from the coil is passed through the

enclosure with a BNC feedthrough, and connects to the platform hardware via BNC

coaxial cable.

In some experiments in which mobility is required, or when the object to be

scanned does not fit in the enclosure, this shielding method is not acceptable. Therefore

we also created a modified probe designed specifically for use without a shielded

enclosure. The RF coil was implemented as a butterfly surface coil consisting of two

adjacent spiral coils wound in opposite direction, and connected in series. When

perturbed with an external B field, each half of the butterfly coil will contribute an equal

and opposite EMF, and thus such external fields induce no overall signal in the coil

(assuming the field is uniform over the entire coil). Magnetization that is local to either

spiral, on the other hand, will cause an unbalanced EMF. This allows butterfly coils to

reject ambient magnetic fields while still being sensitive to local magnetization.

Additionally, the coil is fitted with a grounded screen, which is fabricated by

etching a single sided PCB (thickness of 1.62 mm). This screen forces all external field

lines to terminate at circuit ground, rather than on the coil itself. The screen is slotted in

order to inhibit eddy currents in its surface that would also shield the B field and reduce

the coil's B1 efficiency. An added benefit of the screen is that it significantly reduces the coupling of the coil to the sample via conservative E fields, which reduces the effect of

sample loading on the coil [22].

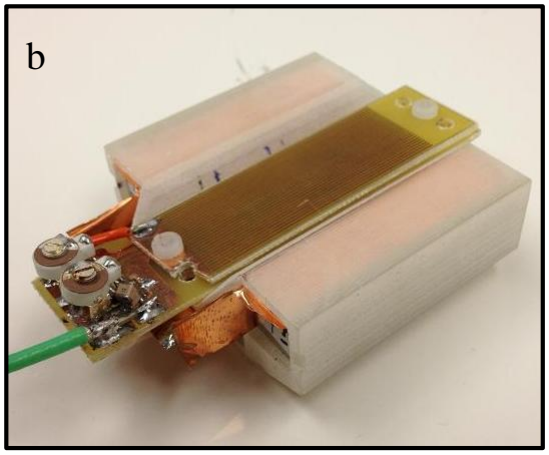
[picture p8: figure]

Figure 2-2-6) Photos of the NMR surface probe. a) The probe uses a butterfly surface coil to null out external B fields. b) External E fields are shielded with the addition of a slotted screen on top of the coil.

These measures do incur a penalty to the sensitivity of the probe, as well as

decreasing the overall penetration depth. However, the loss in sensitivity is more than

compensated for by the immunity to interference (which would otherwise be many times

the thermal noise floor of the system).

2-3 Transmit Receive Switch (TRSW)

Systems using only one coil for transmit and receive require a transmit/receive

switch (TRSW) in order to change whether the coil is coupled to the transmit power

amplifier during the transmit phase or the RF receive chain during the receive phase. A

TR switch has three ports: TX, RX, and Coil. When transmitting, the TX and Coil ports

will be coupled together, and isolated from RX. When receiving, the RX and Coil ports

will be coupled together, and isolated from TX.

The performance of a TR switch is judged based on the isolation and attenuation

between the ports in both states of operation. Attenuation between TX and Coil during the transmit state should be low in order to not severely impact the overall efficiency of

the TPA. Attenuation between Coil and RX during the receive state must be low in order

to not severely degrade the overall SNR of the system. Isolation between Coil and RX

during the transmit state must be enough so that the receive chain is not damaged by

power leaking through. Isolation between TX and RX during the receive state must be

high in order to prevent significant DC artifacts at baseband.

We utilized a broadband TRSW design using MA4P7470F-1072T PIN diodes

[24] from M/A-COM Technology Solutions. The TRSW is composed of two single-pole

single-throw (SPST) switches, each of which can be controlled independently. Each PIN

diode is biased with a negative voltage Vr while in the off state, and is forward biased

with 105 mA of current in the on state. Each of the SPST switches is controlled by its

own logic input signal, called TXSW and RXSW.

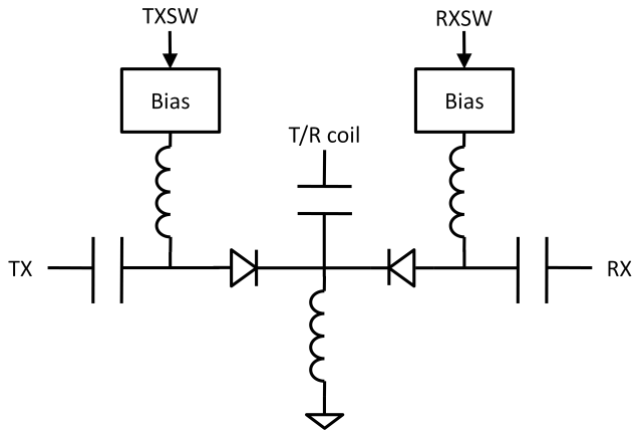
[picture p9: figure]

Figure 2-3-1) Simplified diagram of the TRSW. Each bias block provides a 105 mA forward bias current to its PIN diode when on, and a -Vr reverse bias voltage when off

We measured the small signal performance of the TRSW using the VNA. All

measurements were performed with an incident power level of 10 dBm, with Vr=-13.5 V.

Of primary importance is the isolation provided between the TX and RX ports, due to the risk of damage to the RF receive chain during RF pulses. The isolation of the TRSW is

shown in figures 2-3-2 and 2-3-3.

Figure 2-3-2) Isolation between TX and RX ports when RXSW is on and TXSW is off

Figure 2-3-3) Isolation between TX and RX ports when RXSW is off and TXSW is on

The Isolation between the TX and RX ports was always less than -35 dB,

suggesting that the RF receive amplifier chain will not be damaged by RF pulses up to 55

dBm, or 316 W (see section 2-4). However, PIN diode switches cannot be linearly

approximated under all conditions, especially in the reverse biased state. If the peak RF

voltage applied to a reverse biased PIN diode causes a positive bias voltage across the diode at any time, it will cause carrier generation inside the PIN diode. Depending on the

magnitude and frequency of this positive bias, the pin diode's intrinsic region may begin

to conduct, causing the switch's isolation to degrade. We therefore apply methodology

proposed by [25] to determine the relationship between the safe operating area (SOA) of

the TRSW and the reverse bias voltage Vr

. Figure 2-3-4 shows the maximum RF power

allowed by this methodology as a function of frequency, and for two different values of

Vr

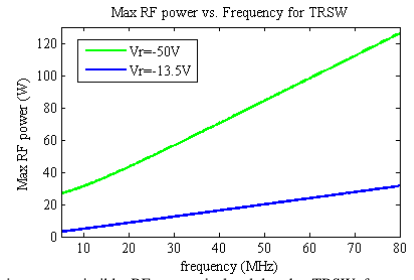
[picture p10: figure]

Figure 2-3-4) Maximum permissible RF power isolated by the TRSW for two example reverse bias voltages. Duty cycle is assumed to be 10%.

We can see that at low frequencies, the maximum power we can safely isolate

with the TRSW is limited by Vr

, especially at low RF frequencies, where Vr must be

approximately equal to the peak RF voltage. For example, at a RF frequency of 8.35

MHz and a Vr of -13.5 V, we are limited to a peak RF voltage of 20.5V, or a RF power of

4.23 W. This is enough for many experiments, such as those done with our solenoid

volume coil, but will be insufficient for most surface coil applications. For such

experiments, we may use a Vr up to -60 V, which allows much higher RF power levels

(though the operation of the TRSW with larger Vr will result in additional artifacts due to

RF chain recovery). The generation of Vr is discussed in greater detail in section 2-8.

Also of interest is the attenuation between the TX and Coil ports during pulse

transmission, and the attenuation between the Coil and RX ports during reception.

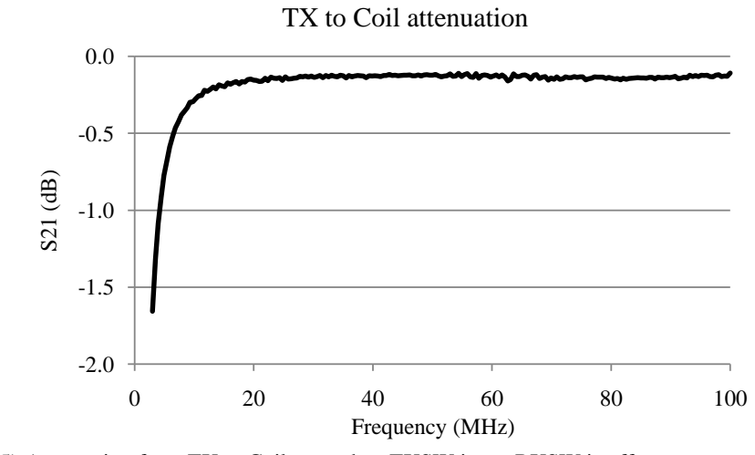
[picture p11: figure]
Frequency (MHz); TX to Coil attenuation

Figure 2-3-5) Attenuation from TX to Coil port when TXSW is on, RXSW is off

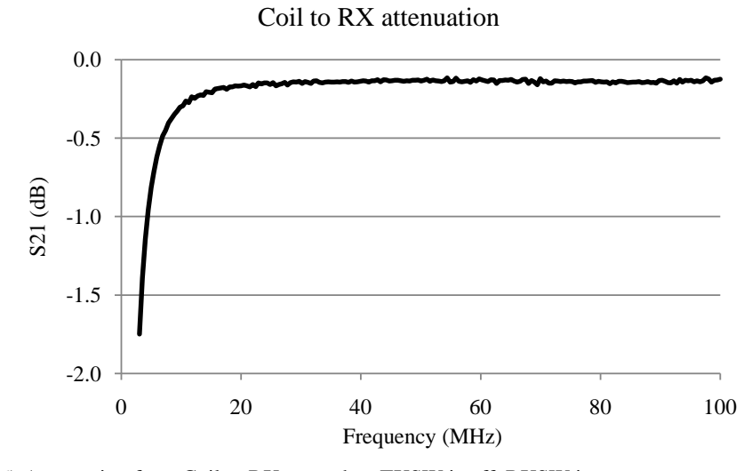
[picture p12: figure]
Frequency (MHz); Coil to RX attenuation

Figure 2-3-6) Attenuation from Coil to RX port when TXSW is off, RXSW is on

It can be seen that the TRSW has a useable bandwidth extending across the entire

measured range (3-100 MHz). However it should be noted that the increase in attenuation

between Coil and RX at frequencies below 10 MHz will have a significant impact on the

system's noise figure (see section 2-6 below).

2-4 Transmit Power Amplifier (TPA)

In order to generate the high B1 necessary for NMR experiments, a RF transmit

power amplifier (TPA) is required. The properties of the TPA, including gain, peak

power, average power, dynamic range, and bandwidth, are dictated by the specific

sequences required, and the RF coil's B1 efficiency and Q. The TPA often allows for

amplitude modulation of the pulse envelope, yielding many different pulse shapes. The

scope of this work deals only with rectangular RF pulses that are only modulated by their

duration, peak amplitude, and phase.

The specifications for the TPA are determined mainly by the desired sequence,

and the RF coil. Therefore we suggest a hypothetical sequence/coil combination that puts

a high demand on the TPA performance. These parameters are based on the spiral surface

coil presented in section 2-2 (see table 2-2-1):

f0 | 8.35 MHz
Maximum flip angle | 180°
Bandwidth of maximum flip angle pulse | 200 KHz
Average Transmit duty cycle | 10%
B1 efficiency | 1.4 mT/A
Coil ESR | 3.877 Ω
Table 2-4-1) Experiment parameters for hypothetical TPA output power.

A rectangular transmit pulse with BW=200 KHz, given by the -3 dB cutoff of the

pulse's frequency spectrum, will be approximately 5 μs in duration. To achieve a 180°

flip angle in 5 μs requires a ω1 of 6.28×10⁵ rad/s. Because this coil generates a linearly

polarized, as opposed to circularly polarized B field, the required B1 amplitude is 4.7 mT.

The pulse will require 3.36 amps peak (2.374 A rms), which gives a power of 21.85 W in

the coil (assuming a lossless matching network). The peak power required is 23.82 W

after factoring the loss of the TRSW. The average power will thus be 2.382 W at the

specified duty cycle.

There are various classes of RF power amplifiers with varying capabilities. Linear

power amplifier classes such as A, B, and C offer simplicity, and the ability to modulate

the output amplitude by varying the input amplitude. They can also be designed to have

wide operating bandwidths. However the linear class amplifiers are inherently inefficient

(generally less than 60%), and a tradeoff between linearity, bandwidth, and efficiency is

necessary [26].

For applications requiring higher power, such as the one specified above, linear

amplifiers are not attractive for small or mobile systems because of their low efficiency.

Switching amplifier topologies, such as classes D, E, and F, boast efficiencies higher than

linear classes [26]. However they must be tuned to a specific frequency range in order to

operate efficiently. Also, they cannot be amplitude modulated by their RF input

amplitude (a method called low level modulation). For these amplifier classes, amplitude

modulation requires modulating the amplifier's supply voltage (a method called high

level modulation), which requires additional circuitry to implement.

For our surface magnet application we chose to construct a TPA based on the

Current Mode Class D (CMCD) topology [27]. While silicon-based devices are well

established for small, mobile linear amplifiers, they have limited efficiencies for very

high frequency switching. For this project, we have adopted gallium-nitride (GaN) FETs,

an emerging transistor technology originally intended for use in switch mode power

supplies [28]. GaN FETs have a heterojunction structure which yields higher electron

mobility than doped silicon. This allows devices to have a low RDSon while maintaining a

very small geometry and fast switching speeds, making them excellent candidates in any

high frequency power switching application. We chose to utilize EPC1005 GaN FETs from EPC as the switching transistors in our CMCD. The FETs are driven by a LM5113

gate driver IC. The RF input from the control board is fed to a LT1713 comparator with

complementary outputs, which provide the logic signals for the LM5113. The TPA can

be deactivated by controlling the logic signal TPAEN, which forces both FETs into an

OFF state. The output of the CMCD is fed to a 1:2 transformer balun that boosts the

output voltage and provides isolation of common mode currents to the TRSW. A

simplified diagram of the CMCD TPA is shown below:

Figure 2-4-1) Simplified schematic of the CMCD TPA

The CMCD topology boasts high efficiency due to the fact that it achieves zero-

voltage-switching (ZVS) on its drains. The parasitic drain to source capacitance (CDS) of

each FET is absorbed into the resonant tank on the output, and therefore does not

contribute to switching losses [27]. Figure 2-4-2 below shows the drain waveforms on

each FET, as well as the total output voltage. All data is collected with the TPA loaded

by a broadband 50 Ω, -38.5 dB attenuator.

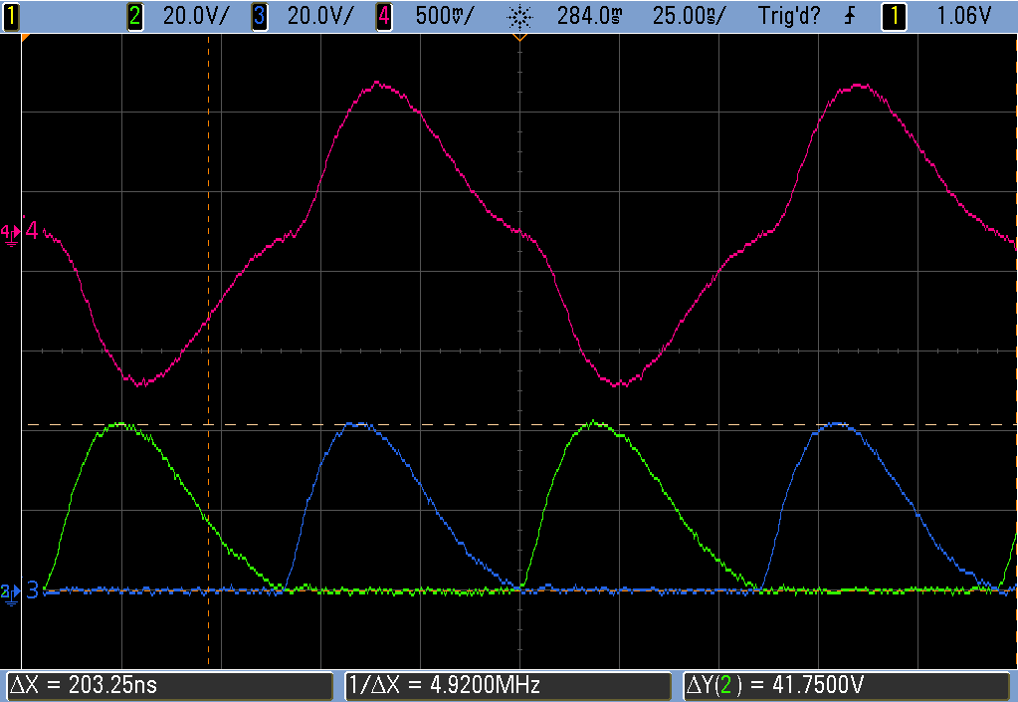
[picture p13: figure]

Figure 2-4-2) Oscilloscope capture of the 8.35 MHz CMCD TPA waveforms. CH2 and CH3 (green and blue, respectively) are the drain voltages of each GaN FET. CH4 (magenta) is the output, after -38.5 dB of attenuation. These waveforms were recorded at full power (VD=12V).

Figure 2-4-3 below shows the spectral content of the RF output at full power, measured

using a CXA series N9000A signal analyzer (SA) from Agilent. The output contains

significant odd harmonics, while even harmonics are suppressed due to the push-pull

operation of the CMCD. Approximately 3.8% of the total output power is lost in these

harmonics.

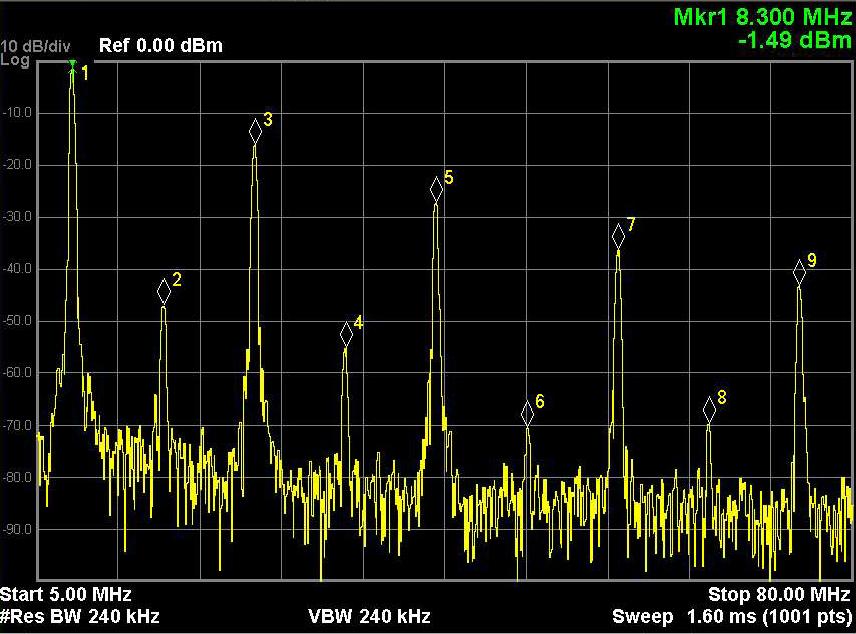
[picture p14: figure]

Figure 2-4-3) Spectral content of the 8.35MHz TPA output at full power (VD=12 V), with -48.5 dB of attenuation. As shown, strong odd harmonics are present, while even harmonics are suppressed.

The efficiency of the TPA was measured by viewing the output power of the

fundamental frequency on the signal analyzer. The RF output was attenuated by -48.00

dB before being fed to the signal analyzer input. The DC supply current, DC supply

voltage, and fundamental power were measured simultaneously during a 150 ms pulse to

calculate power draw and power output, and thus efficiency. These measurements of

power consumption include only power drawn from the TPA output stage (drain power),

and do not include power for the control circuitry or the RF input. The power drawn by

the control circuitry at 8.35 MHz was separately measured to be 0.14 A at 12 V

(independent of output power level), while the RF input power was 0 dBm. This

additional information can be used to calculate the overall power added efficiency (PAE)

of the TPA.

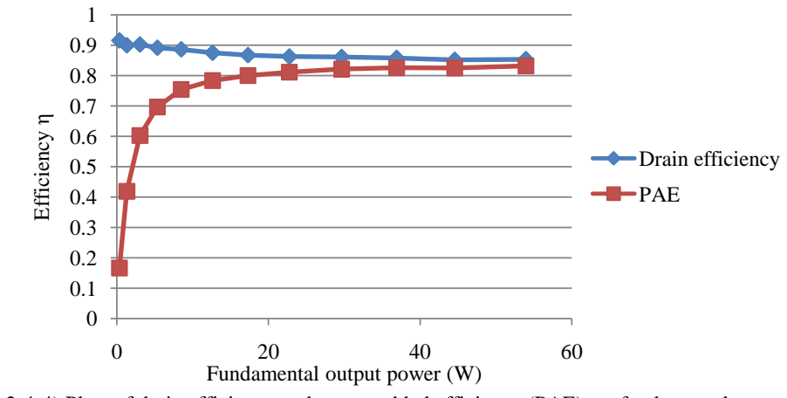
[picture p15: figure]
Efficiency; Fundamental output power (W); Drain efficiency; PAE

Figure 2-4-4) Plots of drain efficiency and power added efficiency (PAE) vs. fundamental output power.

The measured output power can also be used to calculate the RMS amplitude of

the fundamental component of the TPA output. The following plot shows the output

amplitude of the TPA vs. VD. There is some loss of linearity at VD<4 V due to the severe

nonlinearity of CDS in the FETs.

Figure 2-4-5) Plot of TPA output amplitude vs. VD. This amplitude is calculated from the power of the fundamental signal. The displayed fit and R²
is derived from measured data with VD between 4 V and 12 V. The fit is extrapolated to VD<4 to show the deviation of the measured data in that range.

2-5 Buck modulator

For controlling the amplitude of the RF pulses, we devised a buck converter that

converts the 12-18 V system supply into a variable 0-12 VDC bias voltage for the TPA.

The buck modulator regulates a constant DC bias VD to the TPA during each RF pulse,

but changes the VD bias in between RF pulses in order to allow each pulse to have

different amplitudes. The buck modulator is not intended to change the shape of the

envelope for RF pulses (other than its overall amplitude).

Because the time between RF pulses can be as little as 30 μs in some experiments,

and because the TPA demands short pulses of high power, it was desirable for the buck

modulator to have a high closed loop bandwidth in order to accurately control the RF

pulse amplitudes. For this reason we utilized a high frequency voltage-mode buck

converter based similar to that demonstrated in [27]. Like the TPA, we also base this

buck converter on GaN FETs from EPC. The converter operates at a switching frequency

of 1.54 MHz, and has an open loop crossover frequency of 300 KHz with a phase margin

of 55 degrees.

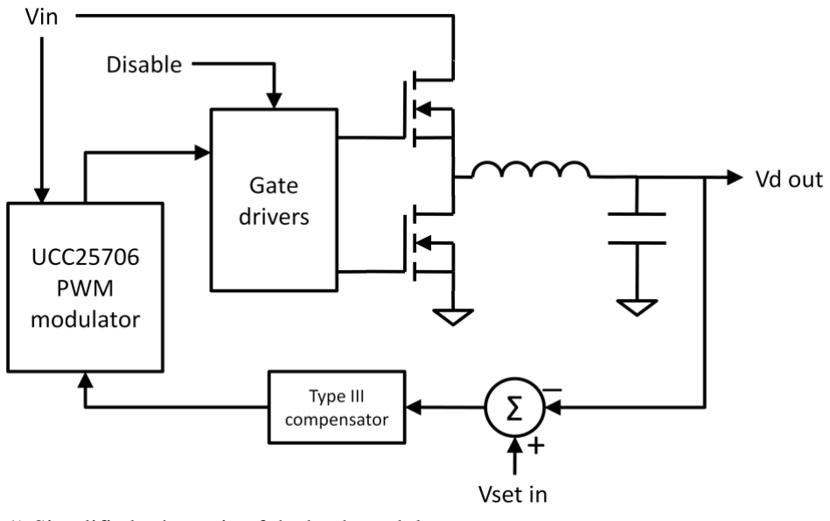
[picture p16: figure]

Figure 2-5-1) Simplified schematic of the buck modulator

Unlike the modulator in [27], our buck modulator did not use RF current feedback

from the TPA, but rather output voltage feedback from VD. VD is controlled by a control

voltage Vset, as shown in figure 2-5-1. The following figures show the transient response

of the buck modulator in response to a step input on its set point. For small signal

conditions, the converter has a rise/fall time of 3.1 μs, and a settling time of 11 μs.

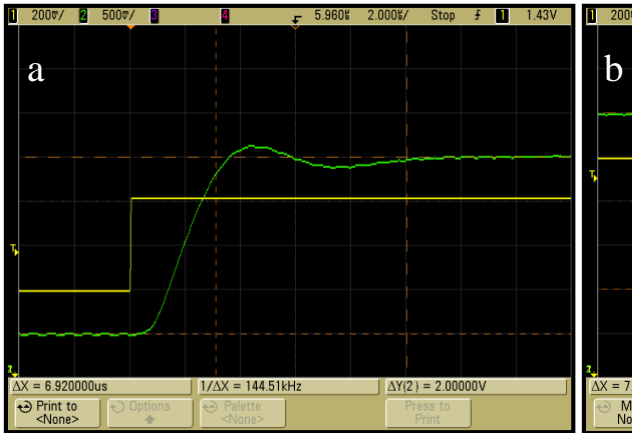
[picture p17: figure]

Figure 2-5-2) Small signal step response of buck modulator between 6 V and 8 V. CH1 (yellow) is the Vset input, and CH2 (green) is the VD output. Trace averaging was performed (N=128) to filter out ripple voltage.

For large signal conditions, in which the duty cycle of the PWM modulator reaches its

limits (0-86%), the response times of the converter are degraded, but still fast enough for

operation with very short pulse spacings (down to 20 μs).

Figure 2-5-3) Large signal step response of buck modulator between 1 V and 10 V. Here the PWM modulator operates in its nonlinear range, causing distortion and slower settling time on the output

The efficiency of the buck modulator was measured by simultaneously measuring

its input and output voltages and currents under varying loads. Measurements were taken

with VD set to both 12 VDC and 6 VDC. Vin was nominally set to 15 VDC. Figure 2-5-4

shows the efficiency results. These measurements include power consumed by the control

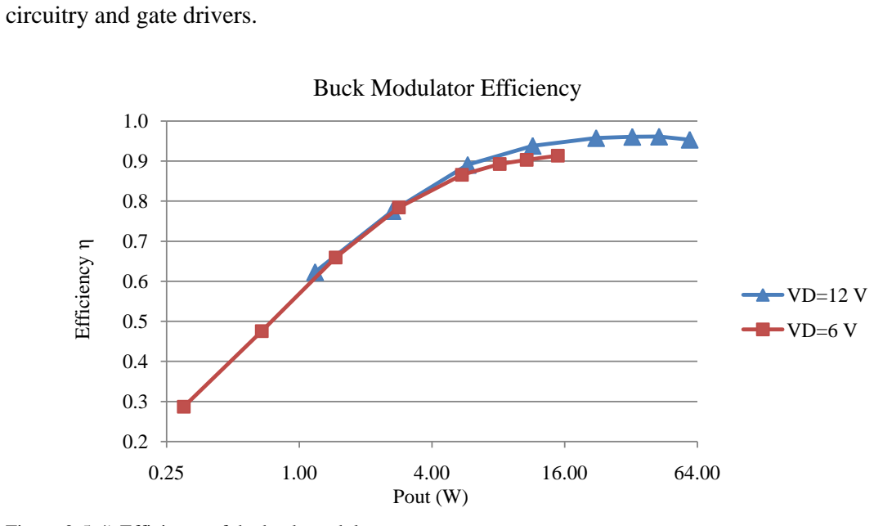
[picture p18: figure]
circuitry and gate drivers.; Buck Modulator Efficiency; Pout (W); Efficiency

Figure 2-5-4) Efficiency of the buck modulator vs. output power

2-6 Low Noise Amplifier and RF Receive Chain (RFamp)

In a typical NMR system, the signal received by the sample magnetization is very

weak and must be amplified significantly before it is sampled by the system. This is done

by a low noise amplifier (LNA). The LNA is often followed by additional RF amplifiers

to provide additional gain, and the combination of these gain stages is called the RF

receive chain. The performance of the overall RF receive chain is primarily described by

its gain and noise figure (NF). The RF chain's noise figure indicates how much the inherent noise of the amplifiers (or any stage in the signal chain) degrades the SNR of the

original signal [29].

The RF receive chain should be designed such that the maximum dynamic range

(DR) of the NMR signal lies completely within the dynamic range of the receive chain. In

this context, dynamic range is described as the range of signal power between the noise

floor and the largest undistorted signal power. The ratio of these power limits is referred

to as the dynamic range ratio (DRR).

The noise floor of an amplifier chain is, assuming no contribution from external

sources, determined by the overall input-referred noise figure, the source impedance, and

the bandwidth. Assuming an impedance match at the source, the noise power at 300K is

[29]:

Noise(dBm) = -174+ NF +10log(BW )
Equation 2-6-1

The NF of the overall system normally is dominated by the NF of the first amplification

stage (the LNA) of the receive chain, and any losses between the signal source and its

input (such as losses in the TRSW). This is demonstrated by the Friis noise formula,

which gives the overall NF of a series of stages with known gains and NFs [29]:

+

+
= | +
1 | 2

3

1

2
1
1 | 1
G G

F
G

F
Ftotal F
Equation 2-6-2

Where in this formula F is noise factor and G is power gain (in linear units). These can be

converted to log units by:

NF =10log( F)
Equation 2-6-3

G 10 log( G) dB =
Equation 2-6-4

In a receive chain, it is desirable for the first stage (called the low noise amplifier, or

LNA) to have high enough gain that the expression for

Ftotal
is dominated by

F1
. It

should also be noticed that any signal attenuation before the first gain stage will

effectively add to the NF.

One of our principle design goals was broadband performance, which allows

operation with a wide range of magnetic fields and different nuclear species. We aimed

for an upper frequency limit of at least 64 MHz, which would allow 1H experiments in

common 1.5 T MRI scanners. We chose an upper frequency limit of 80MHz in order to

ensure sufficient margin for this requirement. For a lower frequency range we chose 5

MHz. This corresponds to a field strength of 117 mT for 1H, which is easily attainable

with small permanent magnet arrays. Due to our desire for a wide operating bandwidth,

we chose the MAR-6SM+ amplifier from Minicircuits for our LNA stage, with a rated

NF of 2.3 dB, Gain=21 dB, and operating frequency range of DC-2 GHz. The MAR-

6SM+ is rated for an absolute maximum input power of +20 dBm (100 mW).

The upper limit of the dynamic range is dependent on the various stages of the RF

chain. Each stage has its own maximum signal power beyond which its effective gain

will begin to decrease significantly. This is often characterized as the input-referred 1 dB

compression point (IP1dB). The RF chain must be designed such that no stage exceeds its

compression point when the maximum signal power is applied. Therefore for the nth stage

of the RF chain, its IP1dB must exceed some level:

∑

=

≥ | +

n

i

dBn | Pin | Gi

IP

1

1 | max
Equation 2-6-5

Where Gi is the gain (in dB) of the ith stage of the chain, and Pinmax is the maximum

expected power (in dBm) at the input of the chain.

Determining the maximum input power Pinmax required estimating the nature of

the actual NMR signal, which is dependent on the sample, the magnet, the coil, and the

sequence. We consider an example experiment performed on the 8.35 MHz surface

sensor and solenoid volume coil (see table 2-2-2) which is designed to yield maximum

signal:

f0 | 8.35 MHz
G0 | 6.52 T/m
RF bandwidth | 100 KHz
Sample | De-ionized Water (DI water)
Maximum sample radius | 5.2 mm
B1 efficiency | 1.24 mT/A
Coil ESR | 0.95 Ω
Table 2-6-1) Experiment parameters for hypothetical NMR signal power.

For this analysis we will use methodology proposed by [12] to estimate experimental

signal and noise power.

The power delivered by a coil with equivalent series resistance R into a matched

load is equal to:

R

P
4

2
= ε
Equation 2-6-6

Where ε is the electromotive force induced by magnetization. The relationship between ε

and the sample magnetic moment is given by:

2 0 | m0 | B1
ε = πf × | ×
Equation 2-6-7

Where f0 is the precession frequency, m0 is the sample magnetic moment, and B1 is the B1

efficiency (in Tesla per amp). The thermal equilibrium magnetic moment m0 from a

sample is given by:

52 ( )
kT

B
m | n | I I
3

1

0

2 2
0 = γ +
Equation 2-6-8

Where n is the number of nuclei, γ is the gyromagnetic ratio of the nuclei, ħ is Planck's

constant, I is the spin of a nuclei, B0 is the static field strength, k is Boltzmann's constant,

and T is absolute temperature. The volume of water excited by the pulses is dependent of

the slice thickness Δy selected by G0 and the pulse bandwidths. For G0=6.52 T/m and

BW=100 KHz, Δy=360 μm, giving an overall excited volume of 3.06x10⁻⁸ m

3
. The

abundance of 1H in water is 6.69×10²⁸ per cubic meter, giving an overall n of 2.047×10²¹

nuclei. The resulting m0 is 1.928×10⁻¹¹ A m²

. The resulting ε will be 1.254×10⁻⁶ V peak,

and the delivered power is 2.08×10⁻¹³ W, or -96.8 dBm. Therefore for this experiment we

needed an overall input referred compression point greater than -96.8 dBm.

For additional gain in the RF signal chain, we chose to use two gain stages after

the LNA, each using the AD8331 variable gain amplifier from Analog Devices. The

AD8331 allows for a voltage controlled gain between -8.5 dB and 37.5 dB, a NF between

4.5 dB and 40 dB (terminated with 50 Ω at input and output, for Vgain range of 0.1-1.0

V), and active input impedance matching. The AD8331 also has an operating bandwidth

from DC to 100 MHz. The wide variable gain range was useful because it allows the

upper limit of the dynamic range to be adjusted for different experiments (for example,

experiments at high field strengths may require a lower gain to avoid compression).

A filter in between the two AD8331 stages may be used in order to limit the

bandwidth of the RF output. This is useful because at high gain settings, large amounts of

noise may cause the output to exceed its IP1dB point. By using a filter to limit the

bandwidth of the receive chain, the total noise power on the output will be decreased,

thus preventing compression without affecting the bandwidth of interest. For all experiments discussed in this work, we used a 3rd order Chebyshev lowpass filter with

fc=20 MHz.

The RF receive chain had a two-way balanced power splitter on its output,

allowing it to connect to the two RF ports of the downconversion stage (see section 2-7).

The loss of the splitter was measured at -3.1 dB, which reduced the overall gain of the RF

chain by 3.1 dB (measured from the input to each of the outputs).

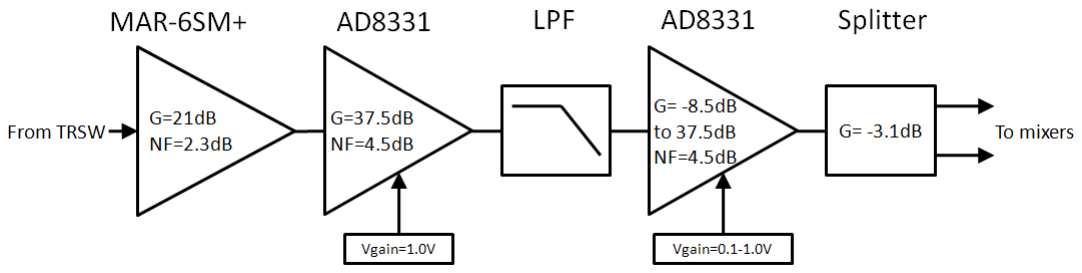
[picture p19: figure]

Figure 2-6-1) Simplified diagram of the RF amplifier chain

The gain of the entire receive chain, including the TRSW, LNA, two AD8331s, and the

splitter were measured using the VNA, and are plotted below.

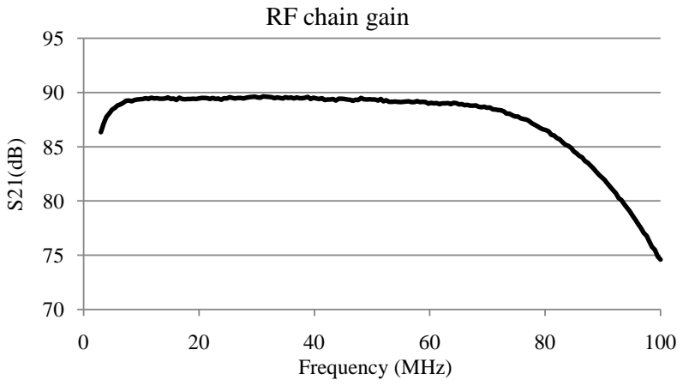
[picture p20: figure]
Frequency (MHz); RF chain gain

Figure 2-6-2) Gain of the RF amplifier chain, with maximum gain for both AD8331 stages

The output referred 1dB compression point (OP1dB) of the RF chain was measured

using the VNA, and was found to be 0.9 dB. So even at maximum gain (89.2 dB at 8.35

MHz) the input referred IP1dB will be -90.1 dBm or greater, satisfying the requirements

for the experiment above.

We also measured the NF of the entire receive chain using the SA and a noise

source (model 346A from Agilent). Measurements were taken over the entire specified

bandwidth, as well as at 8.35 MHz and 63.6 MHz (the Larmor frequencies for 1H at 196.1

mT and 1.5 T, respectively). These measurements were taken with the gain control

voltage of the second AD8331 stage lowered to 0.8 V, in order to avoid output

compression during the test. The results are shown in figure 2-6-3 below:

Figure 2-6-3) Measured NF of the RF amplifier chain, including the RXSW

For frequencies above 10 MHz, the NF of the RF chain is less than 3 dB. Under 10 MHz,

the NF rises sharply, mostly due to the increased loss of the TRSW at such low

frequencies. It should also be noted that the noise source used is not specified for

measurement frequencies under 10 MHz, and therefore the NF measurements at lower

frequencies may not be accurate.

2-7 Downconversion and sampling

Though the NMR signal is limited to a small bandwidth centered at f0, the

sampled signal is best analyzed in the rotating reference frame. This requires

downconverting the signal to baseband. There are various methods of downconversion

and filtering, using both analog and digital techniques. The goal of all downconversion

methods is to preserve the sampled signal and reject signals outside the bandwidth of

interest.

For our system we chose to use frequency mixers. Frequency mixers are devices

with three ports, called RF, IF, and LO (respectively abbreviated for radiofrequency,

intermediate frequency, and local oscillator). The RF signal (centered around f0) to be

downconverted is fed to the RF port, while a carrier signal with frequency fLO is fed to

the LO port. The mixer multiplies the signals on the RF and LO ports, and presents the

product on the IF port. The result is two images (or sidebands) of the RF signal, now

located at (f0-fLO) and (f0+fLO), each with half the original amplitude of the RF signal

[30]. Normally only one of these images is desired, and the other is filtered off. Figure 2-

7-1 shows the process of frequency mixing in the frequency domain.

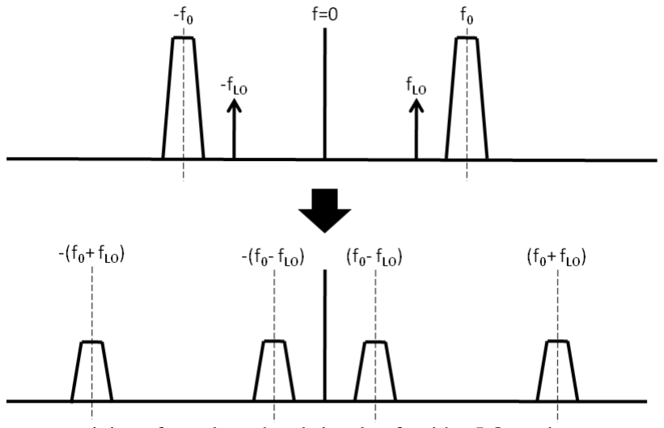
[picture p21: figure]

Figure 2-7-1) Frequency mixing of a real passband signal at f0 with a LO carrier.

We chose to use a zero-IF downconversion system. In a zero-IF system, fLO is set

exactly to f0, and the downconverted IF signal is centered at 0 Hz, and is therefore a

baseband signal. Zero-IF downconversion simplifies the receive chain by eliminating the

need for multiple frequency conversion stages, and only requiring lowpass baseband

filters (as opposed to bandpass IF filters). To recover all information from the RF signal,

two mixers are needed with orthogonal LO carriers, and both their outputs must be

sampled together. This is referred to as quadrature detection [31].

For our frequency mixers, we chose to use the ADE-1L from Minicircuits. The

RF ports were fed from the outputs of the 1:2 splitter in the RF receive chain. The LOs of

the mixers were derived from the outputs of the direct digital synthesis (DDS) subsystem

described in section 2-8 below. The independent DDS channels were used to phase shift

the two LOs by 90°, thus allowing the mixers to output the in phase (I) and quadrature

(Q) components of the RF signal.

The IF ports of both mixers were terminated with 50 Ω to preserve impedance

matching on the RF ports. Baseband amplifiers were then used to amplify, bias, and filter

the IF signals before being sampled by the ADC. The baseband filters were implemented

as third order Bessel lowpass filters with fc=180 KHz, and a passband gain of 23.8 dB.

We implemented the analog to digital conversion using a LTC1407A-1 14 bit, 2

channel simultaneous sampling ADC from Linear Technology. The ADC used an

external voltage reference of 3.0V, and the baseband amp biased both IQ channels at half

the reference voltage. The microcontroller firmware was capable of sampling rates of up

to 577 Ksps on each channel, allowing digitization of baseband signals with frequencies

up to 288.5 KHz (or RF signals with 577 KHz of bandwidth).

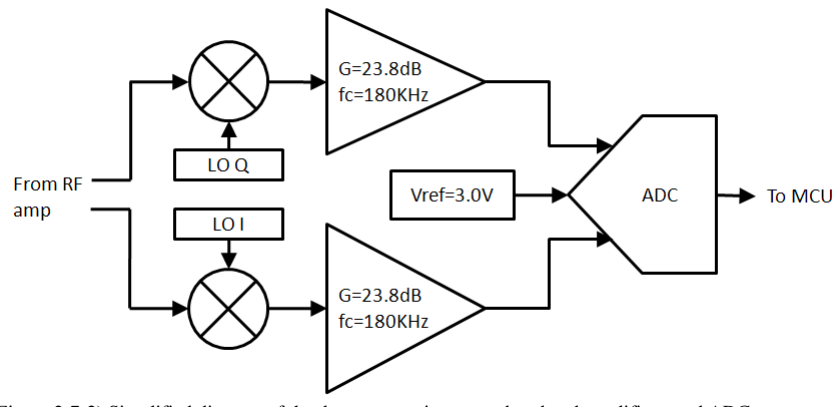
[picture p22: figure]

Figure 2-7-2) Simplified diagram of the downconversion stage, baseband amplifiers, and ADC

The overall conversion gain of this system, including the mixers and baseband

amplifiers, was 18.5 dB (measured from the RF ports to each of the ADC inputs). Its

noise figure is estimated to be 5.3 dB (equal to the conversion loss of the mixers). The

large gain of the RF chain ensures that the contribution of the downconverters to the

overall signal chain NF is negligible.

The downconversion and baseband stage has its own compression point, which in

this case is dominated by the 3.0 V (or 13.55 dBm) full scale range of the ADC. This

gives an IP1dB at the downconverter RF inputs of -3.95 dBm. This is lower than the

OP1dB of the RF chain, meaning that the upper limit of the system dynamic range is

dominated by the downconversion/baseband stage. Thus at maximum gain, the system

IP1dB will be -93.15 dBm, and that will be the upper limit of the system dynamic range

(at maximum RF gain).

The lower limit of the dynamic range is given by the input referred noise power

within the bandwidth of interest. Applying equation 2-6-1 to this experiment (BW=100

KHz, NF=3.01 dB) yields an input referred noise power of -121 dBm. For maximum gain, the overall input referred dynamic range will be -121 dBm through -94.15 dBm, and

the dynamic range ratio will be 26.85 dB. The example experiment described in section

2-6 fits comfortably within this range. Though the DRR seems low, this is a worst-case

result, which can be increased simply by decreasing the gain of the RF amplifier chain.

With a the RFamp gain set to minimum (Vgain=0.1 V), the upper limit of dynamic range

increases to -48.5 dBm, and the dynamic range ratio increases to 72.85dB.

2-8 Control System

The role of the control system is to synthesize and sample all necessary signals in

the NMR system and execute the desired experiments. A control system must have at

least a microprocessor (MCU) or programmable logic device (PLD) for timing of

sequence events, interface with external peripherals, and various ADC and DAC

capabilities. Often the real-time execution of the sequence and the analysis of data are

done on separate systems.

Our control system was based on the AT32UC3C1512C microcontroller from

Atmel. The MCU has a 32 bit architecture and operates at a maximum clock speed of 60

MHz. The AT32UC3C1512 was chosen mainly because in addition to being much more

powerful than 8 bit RISC architecture MCUs, it has a relatively simple toolchain

compared to sophisticated ARM MCUs, and therefore was a good compromise between

performance and ease of development. The MCU controls the operation of the system

through the use of several built in and external peripherals, as shown in figure 2-8-1.

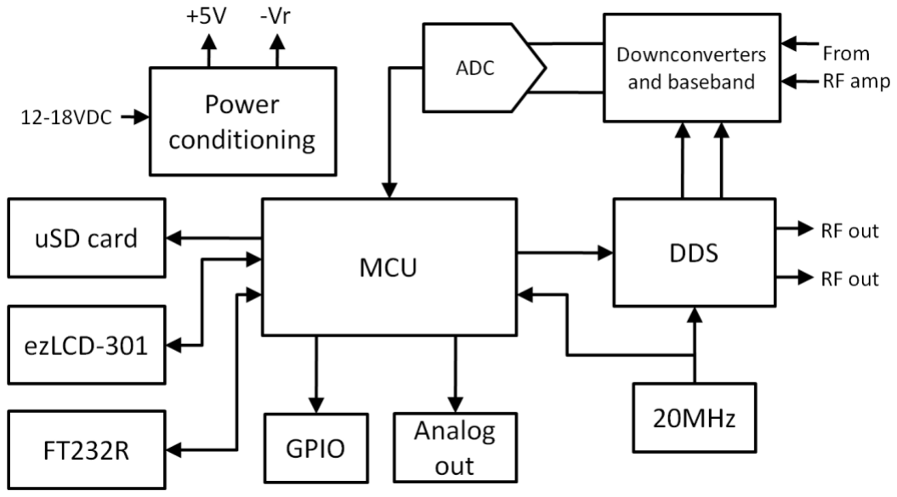
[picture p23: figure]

Figure 2-8-1) Block diagram of the control board and its various peripherals

Direct Digital Synthesis (DDS) RF synthesis

In order to create the necessary pulse sequences, it is desirable to have an RF

synthesizer that is agile in both phase and amplitude, and has excellent frequency

resolution. Direct digital synthesis (DDS) systems fulfill this role. The DDS also provides

the LO signals for homodyne downconversion. Because of this requirement for two

simultaneous, but separate RF channels, we chose the AD9958 from Analog devices. The

AD9958 contains two separate channels (CH0 and CH1) that can be independently

configured, but are internally synchronized, allowing them to be phase and frequency

agile while eliminating the possibility of frequency or phase offsets between the

channels. The AD9958 was controlled by the MCU via a Serial Peripheral Interface (SPI)

bus, as well as several GPIO signals. In our application, we configured the DDS to have

agile amplitude modulation, allowing the RF amplitude to be controlled by simply

toggling GPIO signals, rather than manipulating registers inside the DDS via SPI. This allowed for excellent timing resolution and consistency to be realized for rectangular RF

pulses.

The AD9958 has a master clock frequency range of 100-500 MHz, allowing for

synthesis of RF at frequencies of up to 200 MHz. We chose a master clock frequency of

300 MHz (derived from the 20 MHz reference oscillator), which allows for synthesis of

frequencies up to 120 MHz. A 3rd order Chebyshev lowpass filter with fc=80 MHz was

fitted to each output, in order to reduce aliased signals propagating to the output ports.

The filtered signals are then amplified with AD8008 amplifiers. Each channel was fed to

a pair of amplifiers (G=15.7 dB), so that each channel could drive two different loads

while preserving isolation between them. The amplifier outputs were given 50 Ω series

resistors, since they were intended to drive 50 Ω matched loads. At maximum amplitude,

each amplifier provided 4 dBm of RF power into a 50 Ω load. One amplifier from each

channel also fed the LO port of one of the mixers. The other amplifier output was fed to a

SMC coax connector to the TPA. Together, the DDS and these amplifiers were able to

fulfill the role of providing a RF source for the TPA, as well as the LOs for both channels

of the downconverter.

Figure 2-8-2) Simplified diagram of the DDS RF synthesis

USART to USB transceiver

For communication with a PC host, the control platform also included a FT232R

universal synchronous/asynchronous receiver/transmitter (USART) to USB transceiver

from FTDI. This allows simple communication with USB hosts using the MCU's USART

port. While the FT232R was rated for USB 2.0 full speed operation (which would be 12

Mbaud/s), the FT232R is only specified for baud rates up to 3 Mbaud, or an effective 300

KB/s. It was found that when transferring large packets of data, the overall write speed

was also impacted by wait states in the host's USB drivers, further limiting the effective

write speed to less than 200 KB/s.

SD flash memory

Many of the envisioned NMR acquisitions require more samples than can be

stored on the MCU's internal SRAM (64 KB). Therefore sampled data must be stored

externally during the acquisition, either by sending it to a PC host via the FT232R

transceiver, or by storing it on some external memory. Also in many experiments, the

average sampling rate during a sequence was too high for the FT232R to transmit it to an

external host. For acquisitions where both of these limitations are present, saving the

sampled data to external memory was the only way to avoid losing data.

To solve this problem, we utilized a SD flash memory card on the control board.

The MCU interfaced with the SD card via a separate SPI bus. The SD had a higher

effective write speed (between 1-2 MB/s vs. 200 KB/s) than the FT232R, and much more

capacity than the MCU (up to 32 GB vs. 64 KB). The high capacity also makes

standalone operation feasible, since many hours of experimental data can be stored on the

SD card for later use by a PC host.

LCD interface

For standalone operation it was necessary to provide an interface which allows the

user to operate the system in the absence of a USB host. We selected the ezLCD-301

from EarthLCD, which is a "smart" LCD module including a resistive touch screen, an

integrated LCD controller, and a microcontroller. The ezLCD-301 interfaces with the

control via a USART, over which ASCII commands are sent. The ezLCD-301 handles all

graphics processing, touch recognition, and display routines, which makes for very fast

and simple development of the standalone UI.

The LCD is only necessary when operation in standalone mode is desired. For

more information on standalone operation, see chapter 3-4.

General Purpose I/O (GPIO)

The control platform also made several of the MCU's general purpose I/O (GPIO)

signals available on headers. These GPIO signals were used to control several of the

peripheral systems:

- TXSW: controls the state of the TXSW of the TRSW
- RXSW: controls the state of the RXSW of the TRSW
- TPAEN: this enables or disables the operation of the TPA. For the CMCD TPA,

this deactivates the gate drive circuitry for the GaN FETs.

- Buck shutdown: this optional signal can put the buck modulator into an idle state

in which both FETs are held off. This prevents interference during the sampling

period.

Analog output

The MCU contains two integrated digital to analog converters (DACs). Each

DAC has 12 bits of resolution and a linear output range of 0.2-2.5 V with a 2.5V

reference voltage. Each DAC output controls one of the following:

- Vset: This is the set point for the buck modulator output. It can set the modulator

output level to between 1 VDC and 12 VDC.

- Vgain: This adjusts the gain of the second AD8331 stage in the RF amplifier

chain. It provides a variable gain range of 46 dB.

Power conditioning

For the operation of the many subsystems, several different DC supply voltages

were required. However, we desired to operate from a single DC supply (Vin) between

12-18 VDC. Therefore we required several DC/DC converters in order to derive the

various required supply voltages. All of the necessary DC/DC converters were

implemented on the control board (with the exception of the buck modulator, and the Vr

generator, each of which had its own PCB).

- Vin to +5VDC: The 5V rail is distributed to most of the peripheral systems,

including the FT232R, the RF receive chain, and the TRSW. The +5V rail is also

used as the input to other DC/DC converters.

- +5VDC to +3.3V (digital): 3.3VDC is used to power the MCU and the DDS I/O

port, as well as the ezLCD-301. This is implemented with a LMZ10501 step

down module.

- +5VDC to +1.8V: 1.8VDC is used to power the analog and digital cores of the

DDS (decoupled from each other with ferrite beads). This is implemented with a

LMZ10501 step down module.

- +5VDC to +3.3V (analog): 3.3VDC is used to power the baseband amplifiers,

and the ADC. This supply was implemented using a low noise LDO regulator,
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

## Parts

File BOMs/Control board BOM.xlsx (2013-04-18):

Part description | MPN | QTY | Part ID on schematic | Distributor | Price per unit | Total price
MCU | AT32UC3C1512C-AZR | 1 | MCU | Digikey | $16.99 | $16.99
DDS | AD9958BCPZ | 1 | DDS | Digikey | $34.90 | $34.90
USB UART transceiver | FT232RL | 1 | FTDI | Digikey | $4.50 | $4.50
ADC | LTC1407ACMSE-1 | 1 | ADC | Digikey | $14.07 | $14.07
Quad op amp | LT1802CS#PBF | 1 | OP3 | Digikey | $7.04 | $7.04
Dual op amp | AD8008ARMZ | 2 | OP1, OP2 | Digikey | $5.70 | $11.40
Single op amp | AD8605ARTZ | 1 | OP4 | Digikey | $1.69 | $1.69
Oscillator | ASFLMPC-20.000MHZ-LR-T | 1 | REFCLK | Digikey | $2.69 | $2.69
Stepdown converter +5V | LMZ22003TZ/NOPB | 1 | 5Vreg | Digikey | $11.77 | $11.77
Stepdown converter +3.3V/+1.8V | LMZ10501SEE/NOPB | 2 | 3.3REG1, 1.8REG | Digikey | $4.02 | $8.04
Inverting charge pump | LT1054CS8#PBF | 1 | PUMP | Digikey | $6.03 | $6.03
LDO +3.3V | LT3060ETS8-3.3#TRMPBF | 1 | 3.3VREG2 | Digikey | $3.01 | $3.01
Reference voltage +3.0V | REF3230AIDBVT | 1 | REF1 | Digikey | $5.18 | $5.18
Reference voltage +2.5V | ADR5041ARTZ | 1 | DREF | Digikey | $0.97 | $0.97
P channel FET | ZXMP6A13FTA | 1 | Q2 | Digikey | $0.59 | $0.59
N channel FET | BSS123 | 1 | Q1 | Digikey | $0.29 | $0.29
Zener diode 9.1V | BZT52C9V1-7-F | 1 | Z1 | Digikey | $0.21 | $0.21
Doubly balanced mixer | ADE-1L | 2 | MX0, MX1 | Minicircuits | $15.95 | $31.90
Balun transformer 1:1 | RFXF9503-TR13 | 1 | T3 | Digikey | $1.75 | $1.75
Balun transformer 1:2 CT | CX2045LNL | 2 | T1, T2 | Digikey | $2.30 | $4.60
Ferrite bead | BLM18PG221SN1D | 8 | FB1-8 | Digikey | $0.29 | $2.32
Inductor 330nH | PM1008-R33K-RC | 2 | LF1, LF2 | Digikey | $0.26 | $0.52
0.1% resistor 0805 | ERA-6 series | 10 | R303, R304, R305, R313, R314, R315, R322-5 | Digikey | $0.63 | $6.30
PTC resettable fuse 250mA | 1206L025YR | 1 | FUSE | Digikey | $0.48 | $0.48
Capacitor 220uF 6.3V | RR70J221MDN1 | 1 | CB403 | Digikey | $0.75 | $0.75
LED yellow | LTST-C171KSKT | 1 | L_RX | Digikey | $0.35 | $0.35
LED green | LTST-C171GKT | 1 | L_TX | Digikey | $0.32 | $0.32
2 pin power header | 1614240000 | 3 | +12Vin, 5Vout, -12Vout | Digikey | $0.72 | $2.16
SMC coax connector | 152119 | 6 | RFIN0, RFIN1, TX0, LO0, TX1, LO1 | Digikey | $6.10 | $36.60
USB mini connector | UX60A-MB-5ST | 1 | USB | Digikey | $1.25 | $1.25
10 pin JTAG header | AWHW10G-0202-T-R | 1 | JTAG | Digikey | $0.51 | $0.51
4 pin header for LCD | DF11-4DP-2DSA(01) | 1 | LCD | Digikey | $0.76 | $0.76
MicroSD card slot | DM3BT-DSF-PEJS | 1 | SD | Digikey | $2.76 | $2.76
Total |  |  |  |  |  | $222.70

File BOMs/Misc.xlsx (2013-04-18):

Part description | MPN | QTY | Part ID on schematic | Distributor | Price per unit | Total price
Touch LCD module | exLCD-301 | 1 | NA | EarthLCD.com | $100.00 | $100.00
Battery pack | 2625 | 1 | NA | Batteryspace.com | $29.95 | $29.95
Universal battery charger | 2350 | 1 | NA | Batteryspace.com | $24.95 | $24.95
Power switch | SRB22A2FBRNN | 1 | NA | Digikey | $0.88 | $0.88
Power plugs | 1638780000 | 9 | NA | Digikey | $1.99 | $17.87
2 pin receptacles | 3-644564-2 | 10 | NA | Digikey | $0.25 | $2.53
Receptacle for LCD cable | DF11-4DS-2C | 1 | NA | Digikey | $0.36 | $0.36
Crimp pins for LCD recaptacle | DF11-22SC | 4 | NA | Digikey | $0.36 | $1.44
uSD card | SDSDQY-004G-A11A | 1 | NA | Newegg | $7.99 | $7.99
Total |  |  |  |  |  | $185.97

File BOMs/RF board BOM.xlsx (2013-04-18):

Part description | MPN | QTY | Part ID on schematic | Distributor | Price per unit | Total price
Broadband LNA | MAR-6SM+ | 1 | LNA | Minicircuits | $1.21 | $1.21
Broadband VGA | AD8331ARQZ | 2 | U1,U2 | Digikey | $10.79 | $21.58
RF splitter | ADP-2-1W | 1 | T3 | Minicircuits | $11.95 | $11.95
Balun 1:2 CT | CX2045LNL | 2 | T1,T2 | Digikey | $2.30 | $4.60
PIN diode | MA4P7470F-1072T | 2 | D1,D2 | Mouser | $8.28 | $16.56
PNP BJT | MMBT5401-TP | 4 | Q1,Q2,Q3,Q5 | Digikey | $0.40 | $1.60
N channel FET | BSS123 | 2 | Q4,Q6 | Digikey | $0.29 | $0.58
Schottky diode | DFLS1150-7 | 2 | D3,D4 | Digikey | $0.59 | $1.18
Dual schottky diode | BAS40-04-V-GS08 | 1 | D5 | Digikey | $0.48 | $0.48
Choke 4.7uH | B82422A1472K100 | 7 | L1-7 | Digikey | $0.52 | $3.64
Ferrite bead | BLM18PG221SN1D | 4 | FB1-4 | Digikey | $0.29 | $1.16
Inductors | PM1008 series | 3 | L8-10 | Digikey | $0.26 | $0.78
Potentiometer 1K | 3223W-1-102E | 1 | POT1,POT2 | Digikey | $3.85 | $3.85
Common mode choke 1.5A | DLW5BTN142SQ2L | 2 | CH9,CH11 | Digikey | $1.34 | $2.68
Common mode choke 0.2A | DLW31SN222SQ2L | 3 | CH7,CH8,CH10 | Digikey | $1.22 | $3.66
2 pin power header | 1614240000 | 2 | 5Vin,-VR | Digikey | $0.72 | $1.44
SMC coax connector | 152119 | 2 | RF OUT | Digikey | $6.10 | $12.20
BNC coax connector | 112404 | 2 | TPA_IN,COIL | Digikey | $3.22 | $6.44
Total |  |  |  |  |  | $95.59

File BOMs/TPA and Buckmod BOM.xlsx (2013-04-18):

Part description | MPN | Qty | Part ID on schematic | Distributor | Price per unit | Total price
Comparator | LT1713CMS8#PBF | 1 | COMP1 | Digikey | $4.02 | $4.02
eGaN FET driver | LM5113SD/NOPB | 2 | U101 | Digikey | $4.29 | $8.58
PWM controller | UCC35705DGK | 1 | PWM | Digikey | $2.51 | $2.51
Single op amp | LT1800CS5#TRMPBF | 2 | OP1,OP2 | Digikey | $3.35 | $6.70
AND gate | SN74LVC1G08DCKR | 3 | U102,U103,U202 | Digikey | $0.40 | $1.20
NOR gate | SN74LVC1G02DCKR | 1 | U203 | Digikey | $0.24 | $0.24
LDO +5V | LM2937IMP-5.0/NOPB | 2 | U104,U205 | Digikey | $1.85 | $3.70
LDO +12V | LM2937IMP-12/NOPB | 1 | U204 | Digikey | $1.85 | $1.85
eGaN FET 100V 25A | EPC2001 | 2 | Q4,Q5 | Digikey | $6.00 | $12.00
eGaN FET 40V 10A | EPC2014 | 2 | Q1,Q2 | Digikey | $2.49 | $4.98
N channel FET | BSS123 | 2 | Q3,Q6 | Digikey | $0.29 | $0.58
Schottky diode | BAT54WS-7-F | 3 | D201-203 | Digikey | $0.34 | $1.02
TVS diode | SMAJ54A | 2 | D1,D2 | Digikey | $0.43 | $0.86
Potentiometer 50ohm | 3223W-1-500E | 4 | POT1-4 | Digikey | $3.85 | $15.40
Buck inductor 1.0uH | HCM0703-1R0-R | 1 | L201 | Digikey | $2.44 | $2.44
Common mode choke 1.5A | DLW5BTN142SQ2L | 3 | CH1-3 | Digikey | $1.34 | $4.02
Common mode choke 0.2A | DLW31SN222SQ2L | 3 | CH4-6 | Digikey | $1.22 | $3.66
Capacitor 120uF 25V | PLV1E121MCL1TD | 2 | CB201,CB203 | Digikey | $2.09 | $4.18
Choke 0.47uH | IHLP1212AEERR47M11 | 1 | FB202 | Digikey | $1.11 | $1.11
Choke 220nH | 9250A-221-RC | 2 | L101,L103 | Digikey | $1.21 | $2.42
Choke 1.0uH | 74F106AP-RC | 2 | L102,L104 | Mouser | $1.63 | $3.26
2 pin power header | 1614240000 | 4 | 12Vin,12Vin2,VDout,VDin | Digikey | $0.72 | $2.88
BNC coax connector | 112404 | 2 | TPA_IN,TPA_OUT | Digikey | $3.22 | $6.44
RF inductor | NA | 1 | L1 | Custom | $0.00 | $0.00
TPA output Balun (hand wound) | BN-61-202 | 1 | T1 | Amidon | $0.80 | $0.80
Total |  |  |  |  |  | $94.85

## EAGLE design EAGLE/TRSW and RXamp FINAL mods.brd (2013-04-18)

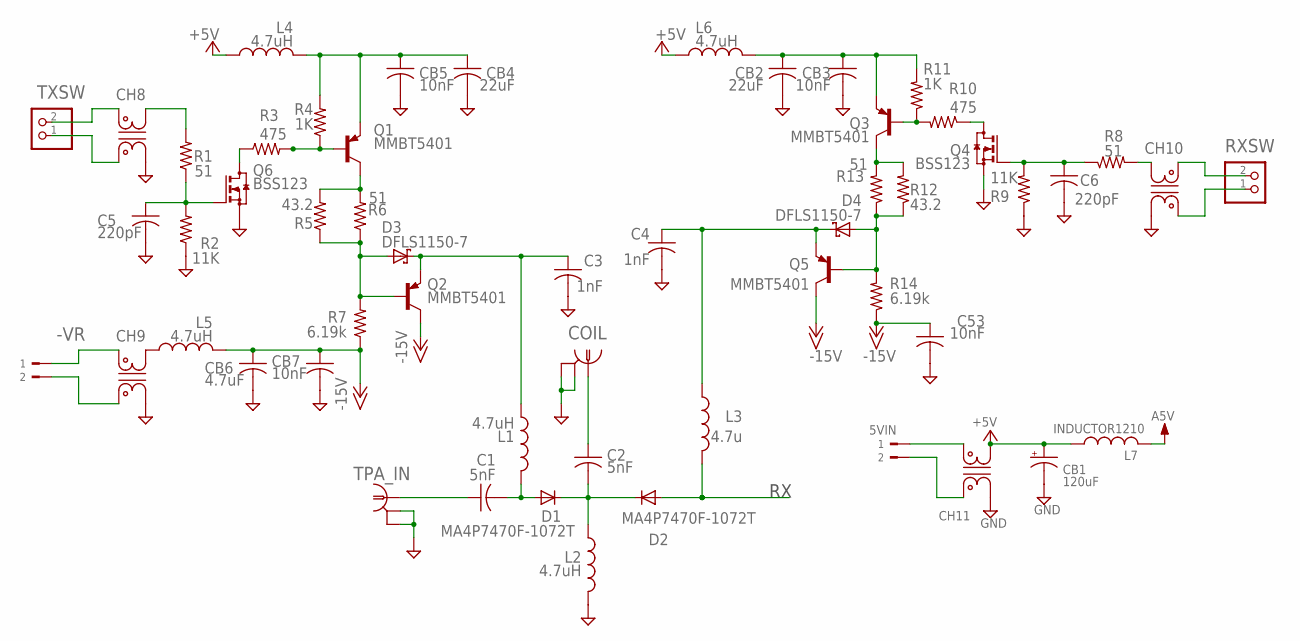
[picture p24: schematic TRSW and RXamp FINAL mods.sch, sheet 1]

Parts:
5VIN: TERM-2OMNIMATE_SL; OMNIMATE_SL_2POS
-VR: TERM-2OMNIMATE_SL; OMNIMATE_SL_2POS
C1, C2: 5nF; 1008
C3, C4: 1nF; C0805
C5, C6: 220pF; C0805
C53: 10nF; C0603
CB1: 120uF; E3,5-8
CB2, CB4: 22uF; C0805
CB3, CB5, CB7: 10nF; C0603
CB6: 4.7uF; C0805
CH8, CH10: CHOKEDLW31S; CHOKE_DLW31S
CH9, CH11: CHOKE; CHOKE_DLW5BT
COIL: BNC-EDGE
D1, D2: MA4P7470F-1072T; 1210-POLAR
D3, D4: DFLS1150-7; POWERDI-123
L1, L2, L4, L5, L6: 4.7uH; 1210
L3: 4.7u; 1210
L7: INDUCTOR1210; 1210
Q1, Q2, Q3, Q5: MMBT5401; SOT23-BEC
Q4, Q6: BSS123; SOT23
R1, R6, R8, R13: 51; R0805
R2, R9: 11K; R0805
R3, R10: 475; R0805
R4, R11: 1K; R0805
R5, R12: 43.2; R0805
R7, R14: 6.19k; R0805
RXSW: PINHD-1X2; 1X02
TPA_IN: BNC-EDGE
TXSW: PINHD-1X2; 1X02

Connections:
+5V: CB1.+, CH11.P$3 (3), L4.1, L6.2, L7.1
-15V: C53.1, CB6.1, CB7.1, L5.2, Q2.C, Q5.C, R7.1, R14.1
A5V: L7.2; also elsewhere on the board
GND: C3.2, C4.2, C5.2, C6.2, C53.2, CB1.-, CB2.2, CB3.2, CB4.2, CB5.2, CB6.2, CB7.2, CH8.P$2 (2), CH9.P$2 (2), CH10.P$2 (2), CH11.P$2 (2), COIL.S1 (GND1), COIL.S2 (GND2), L2.2, Q4.2 (S), Q6.2 (S), R2.1, R9.1, TPA_IN.S1 (GND1), TPA_IN.S2 (GND2); also elsewhere on the board
LNAIN: D2.A, L3.2; also elsewhere on the board
unnamed: D3.A, Q2.B, R5.1, R6.1, R7.2
unnamed: C3.1, D3.K (C), L1.1, Q2.E
unnamed: Q1.C, R5.2, R6.2
unnamed: Q1.B, R3.2, R4.1
unnamed: CH9.P$3 (3), L5.1
unnamed: C1.P$1 (1), TPA_IN.I (1)
unnamed: C1.P$2 (2), D1.A, L1.2
unnamed: C2.P$2 (2), D1.K (C), D2.K (C), L2.1
unnamed: CH8.P$3 (3), R1.2
unnamed: C2.P$1 (1), COIL.I (1)
unnamed: CH10.P$3 (3), R8.2
unnamed: CH10.P$4 (4), RXSW.2
unnamed: CH10.P$1 (1), RXSW.1
unnamed: CH8.P$4 (4), TXSW.2
unnamed: CH8.P$1 (1), TXSW.1
unnamed: 5VIN.1, CH11.P$4 (4)
unnamed: 5VIN.2, CH11.P$1 (1)
unnamed: -VR.1, CH9.P$4 (4)
unnamed: -VR.2, CH9.P$1 (1)
unnamed: D4.A, Q5.B, R12.1, R13.1, R14.2
unnamed: C4.1, D4.K (C), L3.1, Q5.E
unnamed: Q3.C, R12.2, R13.2
unnamed: Q3.B, R10.2, R11.1
unnamed: C6.1, Q4.1 (G), R8.1, R9.2
unnamed: Q6.3 (D), R3.1
unnamed: Q4.3 (D), R10.1
unnamed: C5.1, Q6.1 (G), R1.1, R2.2
unnamed: CB4.1, CB5.1, L4.2, Q1.E, R4.2
unnamed: CB2.1, CB3.1, L6.1, Q3.E, R11.2

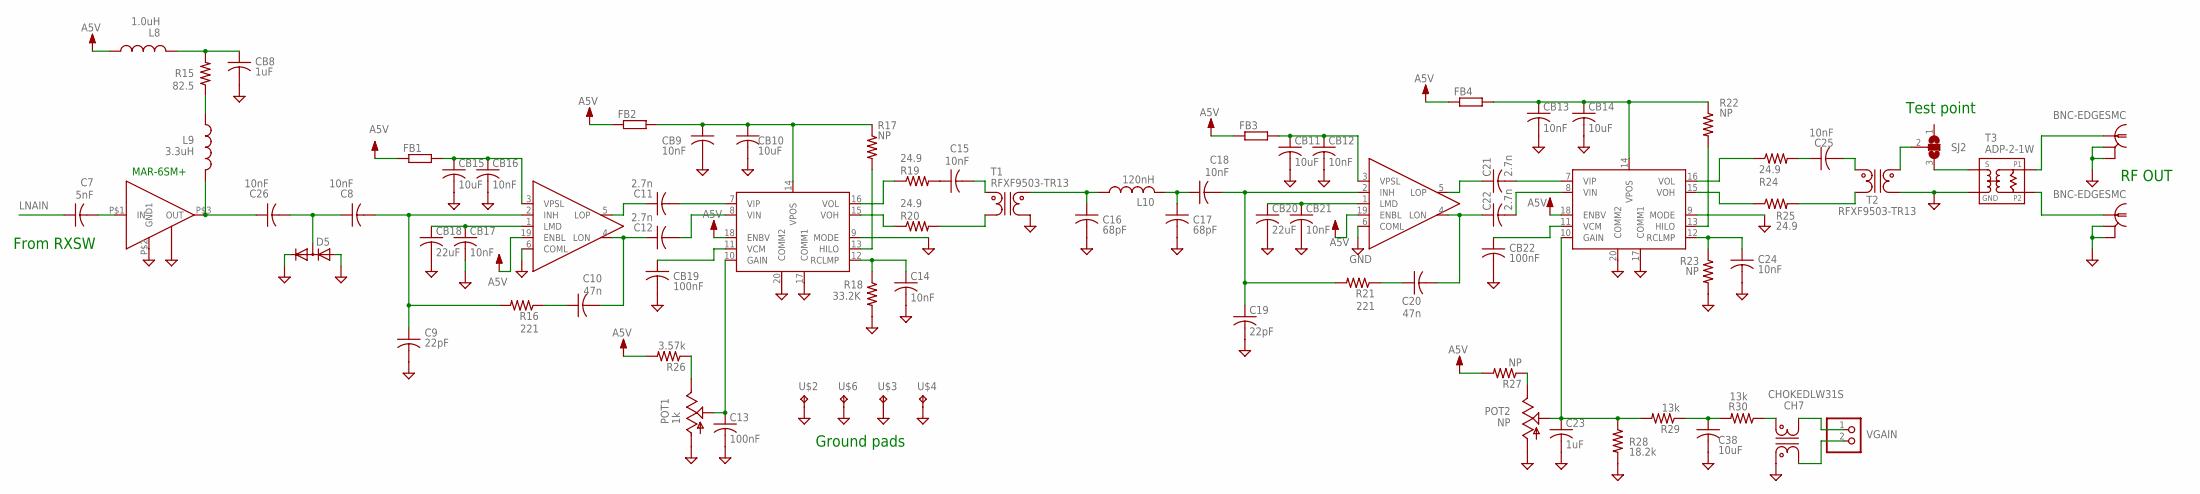
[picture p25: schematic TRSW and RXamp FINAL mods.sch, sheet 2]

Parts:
C7: 5nF; 1008
C8, C18, C26: 10nF; C0805
C9, C19: 22pF; C0805
C10, C20: 47n; C0805
C11, C12, C21, C22: 2.7n; C0603
C13: 100nF; C0603
C14, C15, C24, C25: 10nF; C0603
C16, C17: 68pF; 1008
C23: 1uF; C0805
C38: 10uF; C0805
CB8: 1uF; C0805
CB9, CB12, CB13, CB16, CB17, CB21: 10nF; C0603
CB10, CB11, CB14, CB15: 10uF; C0805
CB18, CB20: 22uF; C0805
CB19, CB22: 100nF; C0603
CH7: CHOKEDLW31S; CHOKE_DLW31S
D5: DIODE_2CACA-SOT23; SOT23
FB1, FB2, FB3, FB4: R-EU_R0603; R0603
L8: 1.0uH; 1008
L9: 3.3uH; 1008
L10: 120nH; 1008
LNA: MAR-6SM+; WW107
POT1: 1k; 3223W
POT2: NP; 3223W
R15: 82.5; R0805
R16, R21: 221; R0805
R17, R22, R23, R27: NP; R0805
R18: 33.2K; R0805
R19, R20, R24, R25: 24.9; R0805
R26: 3.57k; R0805
R28: 18.2k; R0805
R29, R30: 13k; R0805
RF_OUT: BNC-EDGESMC; SMC-EDGE
SJ2: SJ2W; SJ_2
T1, T2: RFXF9503-TR13; CX20XX_BALUN
T3: ADP-2-1W; CD636
U1, U2: AD8331; QSOP-20
U$2, U$3, U$4: TESTPOINTKEYSTONE_ELECTRONICS_5016; SMD_TESTPAD
U$6: SOLDERPADSMALL; PAD-SMALL
U$27: BNC-EDGESMC; SMC-EDGE
VGAIN: PINHD-1X2; 1X02

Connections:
A5V: FB1.1, FB2.1, FB3.1, FB4.1, L8.P$1 (1), R26.2, R27.2, U1.18 (ENBV), U1.19 (ENBL), U2.18 (ENBV), U2.19 (ENBL); also elsewhere on the board
GND: C9.2, C13.2, C14.2, C16.P$2 (2), C17.P$2 (2), C19.2, C23.2, C24.2, C38.2, CB8.2, CB9.2, CB10.2, CB11.2, CB12.2, CB13.2, CB14.2, CB15.2, CB16.2, CB17.2, CB18.2, CB19.2, CB20.2, CB21.2, CB22.2, CH7.P$1 (1), D5.1 (A), D5.2 (C), LNA.P$2 (GND1), LNA.P$4 (GND2), POT1.1 (A), POT2.1 (A), R18.2, R23.2, R28.2, RF_OUT.2 (GND1), RF_OUT.3 (GND2), T1.P$3 (3), T2.P$3 (3), T3.P$6 (GND), U1.6 (COML), U1.9 (MODE), U1.17 (COMM1), U1.20 (COMM2), U2.6 (COML), U2.9 (MODE), U2.17 (COMM1), U2.20 (COMM2), U$2.P$1, U$3.P$1, U$4.P$1, U$6.P$1, U$27.2 (GND1), U$27.3 (GND2); also elsewhere on the board
LNAIN: C7.P$1 (1); also elsewhere on the board
unnamed: C16.P$1 (1), L10.P$1 (1), T1.P$4 (4)
unnamed: C17.P$1 (1), C18.1, L10.P$2 (2)
unnamed: C8.2, C9.1, R16.2, U1.2 (INH)
unnamed: CH7.P$4 (4), R30.1
unnamed: CH7.P$3 (3), VGAIN.1
unnamed: CH7.P$2 (2), VGAIN.2
unnamed: C8.1, C26.2, D5.3 (AC)
unnamed: C26.1, L9.P$2 (2), LNA.P$3 (OUT)
unnamed: L9.P$1 (1), R15.1
unnamed: CB8.1, L8.P$2 (2), R15.2
unnamed: C7.P$2 (2), LNA.P$1 (IN)
unnamed: C11.1, U1.5 (LOP)
unnamed: C11.2, U1.7 (VIP)
unnamed: C12.2, U1.8 (VIN)
unnamed: C10.2, C12.1, U1.4 (LON)
unnamed: C15.1, R19.2
unnamed: C10.1, R16.1
unnamed: CB17.1, CB18.1, U1.1 (LMD)
unnamed: CB15.1, CB16.1, FB1.2, U1.3 (VPSL)
unnamed: CB19.1, U1.11 (VCM)
unnamed: R19.1, U1.16 (VOL)
unnamed: R20.1, U1.15 (VOH)
unnamed: C14.1, R18.1, U1.12 (RCLMP)
unnamed: CB9.1, CB10.1, FB2.2, R17.1, U1.14 (VPOS)
unnamed: R20.2, T1.P$1 (1)
unnamed: R17.2, U1.13 (HILO)
unnamed: C15.2, T1.P$5 (6)
unnamed: C13.1, POT1.2 (S), U1.10 (GAIN)
unnamed: POT1.3 (E), R26.1
unnamed: C18.2, C19.1, R21.2, U2.2 (INH)
unnamed: C21.1, U2.5 (LOP)
unnamed: C21.2, U2.7 (VIP)
unnamed: C22.2, U2.8 (VIN)
unnamed: C20.2, C22.1, U2.4 (LON)
unnamed: C20.1, R21.1
unnamed: CB20.1, CB21.1, U2.1 (LMD)
unnamed: CB11.1, CB12.1, FB3.2, U2.3 (VPSL)
unnamed: CB22.1, U2.11 (VCM)
unnamed: R24.1, U2.16 (VOL)
unnamed: R25.1, U2.15 (VOH)
unnamed: C24.1, R23.1, U2.12 (RCLMP)
unnamed: CB13.1, CB14.1, FB4.2, R22.1, U2.14 (VPOS)
unnamed: R22.2, U2.13 (HILO)
unnamed: C25.1, R24.2
unnamed: R25.2, T2.P$1 (1)
unnamed: C25.2, T2.P$5 (6)
unnamed: C23.1, POT2.2 (S), R28.1, R29.2, U2.10 (GAIN)
unnamed: POT2.3 (E), R27.1
unnamed: T3.P$4 (P2), U$27.1
unnamed: RF_OUT.1, T3.P$3 (P1)
unnamed: SJ2.2, T2.P$4 (4)
unnamed: SJ2.3, T3.P$1 (S)
RTY5: C38.1, R29.1, R30.2

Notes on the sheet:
Ground pads
Test point
RF OUT
From RXSW
MAR-6SM+

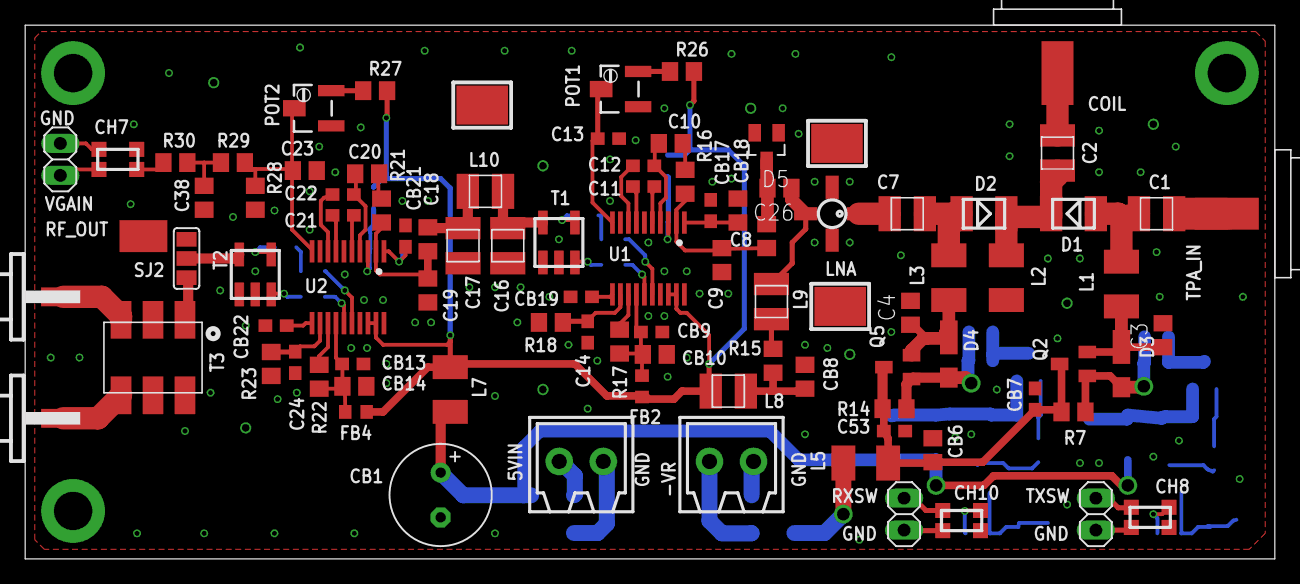
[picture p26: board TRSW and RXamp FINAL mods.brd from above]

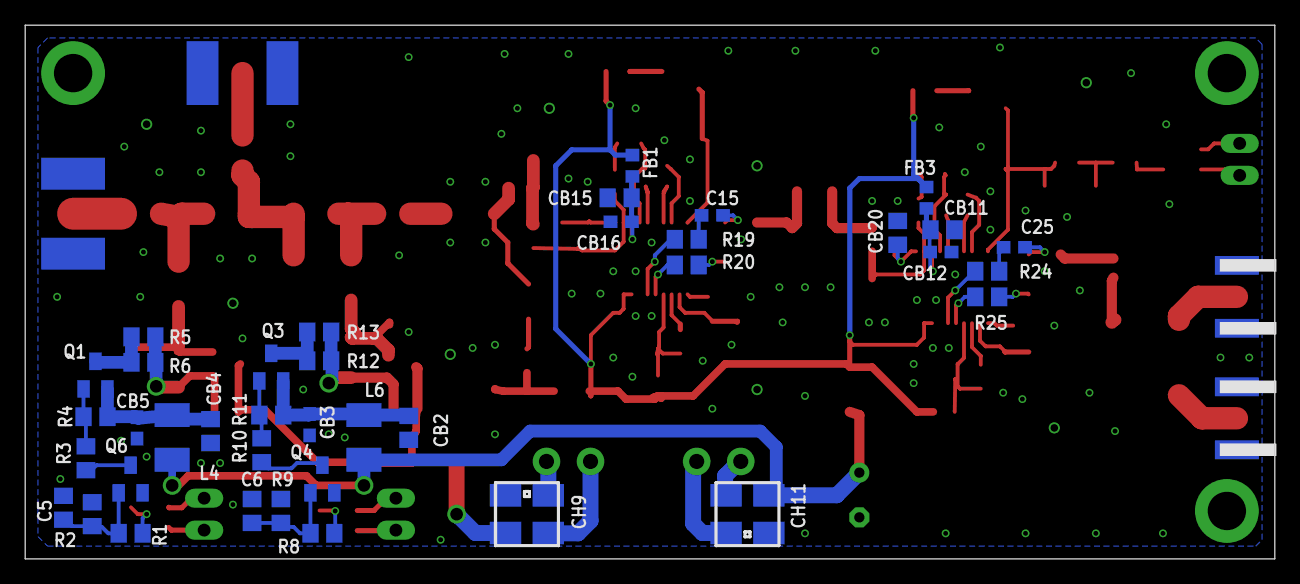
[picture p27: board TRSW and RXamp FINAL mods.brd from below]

Board: 4 copper layers, 99.3 x 42.4 mm, 132 parts (39 on the bottom side), 87 nets.

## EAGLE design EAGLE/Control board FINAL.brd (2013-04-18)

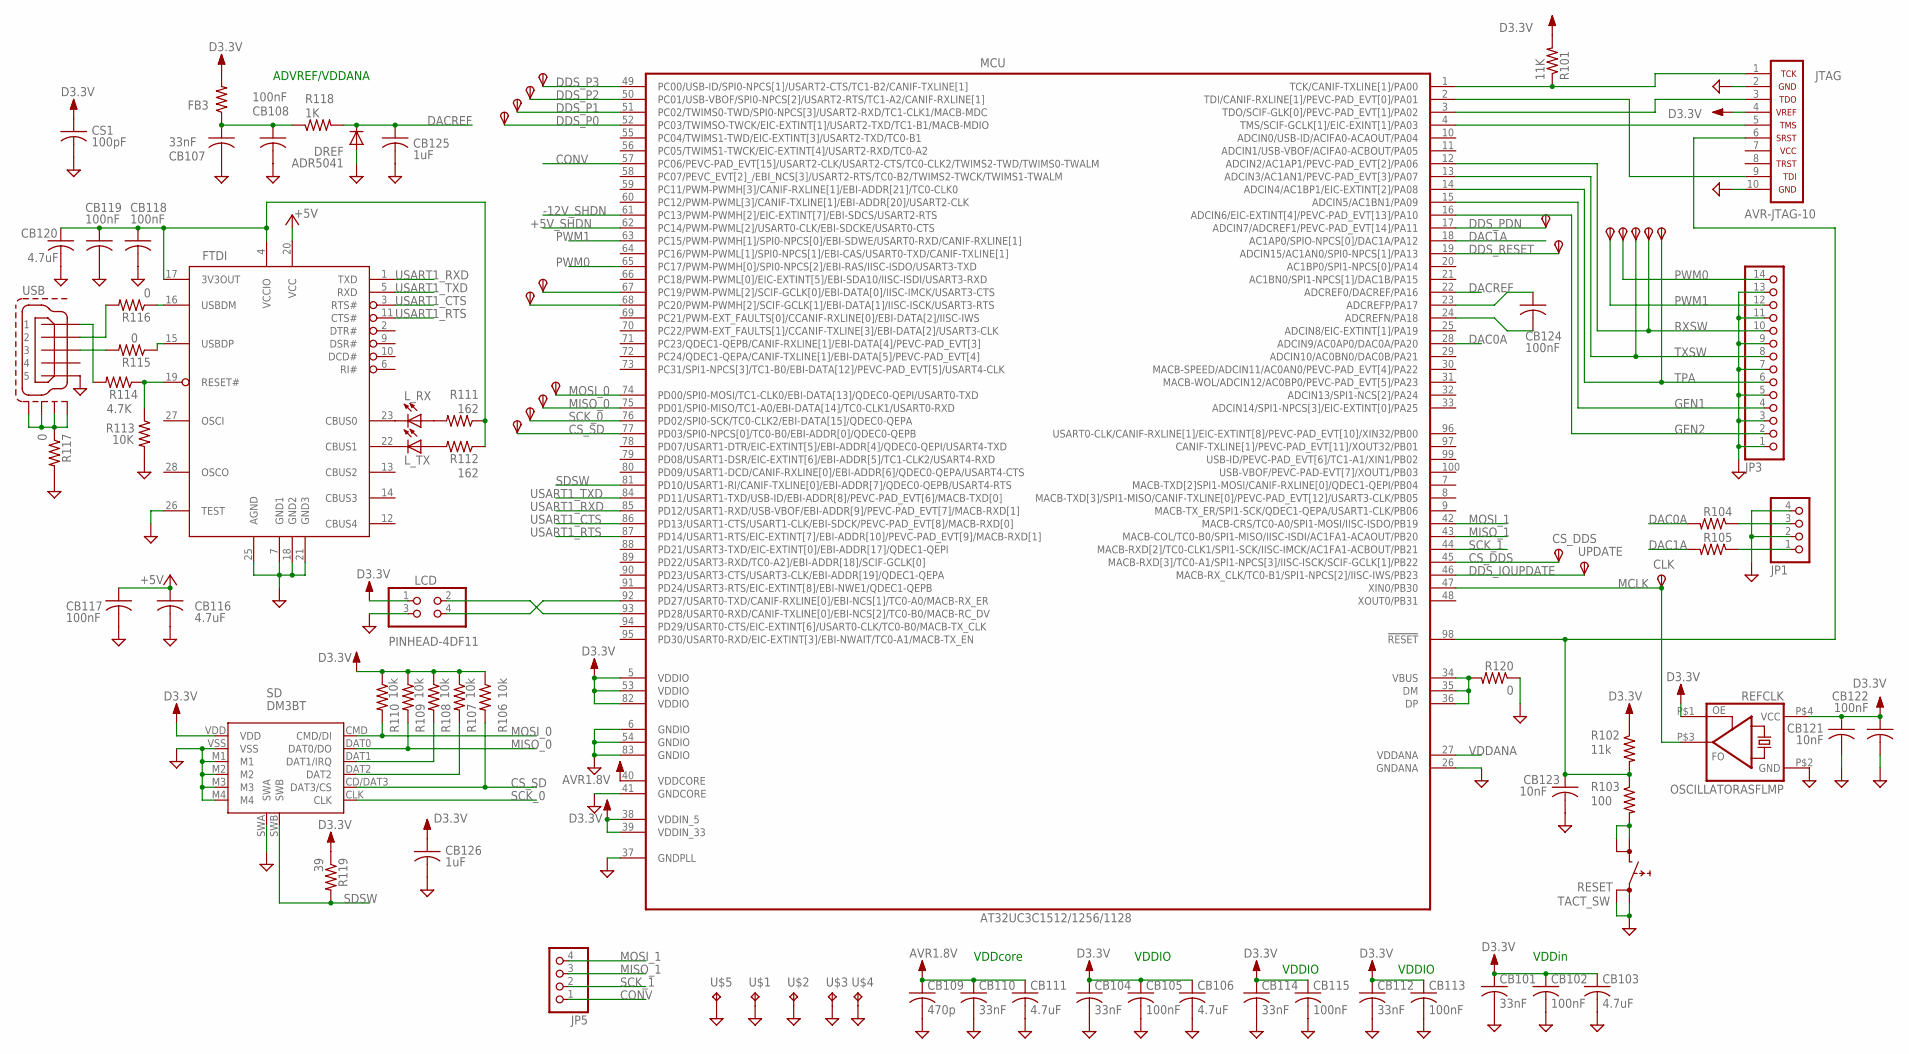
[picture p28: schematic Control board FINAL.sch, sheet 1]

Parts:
CB101, CB104, CB107, CB110, CB112, CB114: 33nF; C0603
CB102, CB105, CB108, CB113, CB115, CB117, CB118, CB119, CB122, CB124: 100nF; C0603
CB103, CB106, CB111, CB116, CB120: 4.7uF; C0805
CB109: 470p; C0603
CB121, CB123: 10nF; C0603
CB125, CB126: 1uF; C0603
CLK: TPSTP10R; TP10R
CS1: 100pF; C0805
CS_DDS: TPSTP10R; TP10R
CS_SD: TPSTP10R; TP10R
DDSPDN: TPSTP10R; TP10R
DDSRESET: TPSTP10R; TP10R
DREF: ADR5041; SOT23-3
FB3: R-US_R0603; R0603
FTDI: FT232RL; SSOP28DB
GCLK0, GCLK1: TPSTP10R; TP10R
JP1, JP5: PINHD-1X4; 1X04
JP3: PINHD-1X14; 1X14
JTAG: AVR-JTAG-10
LCD: PINHEAD-4DF11; DF11-4POS
L_RX: LEDCHIPLED_0805; CHIPLED_0805
L_TX: LEDCHIPLED_0805; CHIPLED_0805
MCU: AT32UC3C1512/1256/1128; TQFP100
MISO0: TPSTP10R; TP10R
MOSI0: TPSTP10R; TP10R
P0, P1, P2, P3: TPSTP10R; TP10R
R101: 11K; R0805
R102: 11k; R0805
R103: 100; R0805
R104, R105: R-US_R0805; R0805
R106, R107, R108, R109, R110: 10k; R0805
R111, R112: 162; R0805
R113: 10K; R0805
R114: 4.7K; R0805
R115, R116, R117, R120: 0; R0805
R118: 1K; R0805
R119: 39; R0805
REFCLK: OSCILLATORASFLMP; QFN4_ASFLMP_OSCILLATOR
RESET: TACT_SW; KMR2_TACT_SWITCH
SCK0: TPSTP10R; TP10R
SD: DM3BT
TP1, TP2, TP3, TP4, TP5: TPSTP10R; TP10R
U$1, U$2, U$3, U$4, U$5: TESTPOINTKEYSTONE_ELECTRONICS_5016; SMD_TESTPAD
UPDATE: TPSTP10R; TP10R
USB: MINI-USB-SHIELD-UX60A-MB-5ST; UX60A-MB-5ST

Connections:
+5V: CB116.1, CB117.1, FTDI.20 (VCC); also elsewhere on the board
+5V_SHDN: MCU.62 (PC14/PWM-PWML[2]/USART0-CLK/EBI-SDCKE/U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); also elsewhere on the board
-12V_SHDN: MCU.61 (PC13/PWM-PWMH[2]/EIC-EXTINT[7]/EBI-SDCS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); also elsewhere on the board
AVR1.8V: CB109.1, CB110.1, CB111.1, MCU.40 (VDDCORE)
CONV: JP5.1, MCU.57 (PC06/PEVC-PAD_EVT[15]/USART2-CLK/USART2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); also elsewhere on the board
CS_DDS: CS_DDS.TP, MCU.45 (MACB-RXD[3]/TC0-A1/SPI1-NPCS[3]/IISC-IS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); also elsewhere on the board
CS_SD: CS_SD.TP, MCU.77 (PD03/SPI0-NPCS[0]/TC0-B0/EBI-ADDR[0]/QD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), R106.2, SD.CD/DAT3 (DAT3/CS)
D3.3V: CB101.1, CB102.1, CB103.1, CB104.1, CB105.1, CB106.1, CB112.1, CB113.1, CB114.1, CB115.1, CB121.1, CB122.1, CB126.1, CS1.1, FB3.2, JTAG.4, LCD.1, MCU.5 (VDDIO), MCU.38 (VDDIN_5), MCU.39 (VDDIN_33), MCU.53 (VDDIO), MCU.82 (VDDIO), R101.2, R102.1, R106.1, R107.1, R108.1, R109.1, R110.1, R119.1, REFCLK.P$1 (OE), REFCLK.P$4 (VCC), SD.VDD; also elsewhere on the board
DAC0A: MCU.28 (ADCIN9/AC0AP0/DAC0A/PA20), R104.2
DAC1A: MCU.18 (AC1AP0/SPIO-NPCS[0]/DAC1A/PA12), R105.2
DACREF: CB125.1, DREF.1 (C), MCU.22 (ADCREF0/DACREF/PA16), R118.2
DDS_IOUPDATE: MCU.46 (MACB-RX_CLK/TC0-B1/SPI1-NPCS[2]/IISC-IW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), UPDATE.TP; also elsewhere on the board
DDS_P0: MCU.52 (PC03/TWIMSO-TWCK/EIC-EXTINT[1]/USART2-T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), P0.TP; also elsewhere on the board
DDS_P1: MCU.51 (PC02/TWIMS0-TWD/SPI0-NPCS[3]/USART2-RXD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), P1.TP; also elsewhere on the board
DDS_P2: MCU.50 (PC01/USB-VBOF/SPI0-NPCS[2]/USART2-RTS/T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), P2.TP; also elsewhere on the board
DDS_P3: MCU.49 (PC00/USB-ID/SPI0-NPCS[1]/USART2-CTS/TC1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), P3.TP; also elsewhere on the board
DDS_PDN: DDSPDN.TP, MCU.17 (ADCIN7/ADCREF1/PEVC-PAD_EVT[14]/PA11); also elsewhere on the board
DDS_RESET: DDSRESET.TP, MCU.19 (ADCIN15/AC1AN0/SPI0-NPCS[1]/PA13); also elsewhere on the board
DGND: USB.5
GEN1: JP3.4, MCU.15 (ADCIN5/AC1BN1/PA09)
GEN2: JP3.2, MCU.16 (ADCIN6/EIC-EXTINT[4]/PEVC-PAD_EVT[13]/P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)
GND: CB101.2, CB102.2, CB103.2, CB104.2, CB105.2, CB106.2, CB107.2, CB108.2, CB109.2, CB110.2, CB111.2, CB112.2, CB113.2, CB114.2, CB115.2, CB116.2, CB117.2, CB118.2, CB119.2, CB120.2, CB121.2, CB122.2, CB123.2, CB125.2, CB126.2, CS1.2, DREF.2 (A), FTDI.7 (GND1), FTDI.18 (GND2), FTDI.21 (GND3), FTDI.25 (AGND), FTDI.26 (TEST), JP1.2, JP1.4, JP3.1, JP3.3, JP3.5, JP3.7, JP3.9, JP3.11, JP3.13, JTAG.2, JTAG.10, LCD.3, MCU.6 (GNDIO), MCU.26 (GNDANA), MCU.37 (GNDPLL), MCU.41 (GNDCORE), MCU.54 (GNDIO), MCU.83 (GNDIO), R113.2, R117.2, R120.1, REFCLK.P$2 (GND), RESET.P$1 (0), RESET.P$3 (0), SD.M1, SD.M2, SD.M3, SD.M4, SD.SWA, SD.VSS, U$1.P$1, U$2.P$1, U$3.P$1, U$4.P$1, U$5.P$1; also elsewhere on the board
MCLK: CLK.TP, MCU.47 (XIN0/PB30), REFCLK.P$3 (FO); also elsewhere on the board
MISO_0: MCU.75 (PD01/SPI0-MISO/TC1-A0/EBI-DATA[14]/TC0-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), MISO0.TP, R109.2, SD.DAT0 (DAT0/DO)
MISO_1: JP5.3, MCU.43 (MACB-COL/TC0-B0/SPI1-MISO/IISC-ISDI/AC1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); also elsewhere on the board
MOSI_0: MCU.74 (PD00/SPI0-MOSI/TC1-CLK0/EBI-DATA[13]/QD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), MOSI0.TP, R110.2, SD.CMD (CMD/DI)
MOSI_1: JP5.4, MCU.42 (MACB-CRS/TC0-A0/SPI1-MOSI/IISC-ISDO/PB19); also elsewhere on the board
unnamed: CB123.1, JTAG.6, MCU.98 (!RESET), R102.2, R103.1
unnamed: JTAG.1, MCU.1 (TCK/CANIF-TXLINE[1]/PA00), R101.1
unnamed: JTAG.9, MCU.2 (TDI/CANIF-RXLINE[1]/PEVC-PAD_EVT[0]/PA01)
unnamed: JTAG.3, MCU.3 (TDO/SCIF-GLK[0]/PEVC-PAD_EVT[1]/PA02)
unnamed: JTAG.5, MCU.4 (TMS/SCIF-GCLK[1]/EIC-EXINT[1]/PA03)
unnamed: JP1.3, R104.1
unnamed: CB118.1, CB119.1, CB120.1, FTDI.4 (VCCIO), FTDI.17 (3V3OUT), R111.1, R112.1
unnamed: R115.2, USB.3
unnamed: R116.2, USB.2
unnamed: FTDI.15 (USBDP), R115.1
unnamed: FTDI.16 (USBDM), R116.1
unnamed: FTDI.19 (RESET#), R113.1, R114.1
unnamed: R114.2, USB.1
unnamed: CB124.2, MCU.24 (ADCREFN/PA18)
unnamed: R103.2, RESET.P$2 (1), RESET.P$4 (1)
unnamed: R108.2, SD.DAT1 (DAT1/IRQ)
unnamed: R107.2, SD.DAT2
unnamed: CB124.1, MCU.23 (ADCREFP/PA17)
unnamed: JP1.1, R105.1
unnamed: R117.1, USB.M1 (S1), USB.M2 (S2), USB.M3 (S3), USB.M4 (S4)
unnamed: MCU.34 (VBUS), MCU.35 (DM), MCU.36 (DP), R120.2
unnamed: FTDI.23 (CBUS0), L_RX.C
unnamed: L_RX.A, R111.2
unnamed: L_TX.A, R112.2
unnamed: FTDI.22 (CBUS1), L_TX.C
unnamed: GCLK0.TP, MCU.67 (PC19/PWM-PWML[2]/SCIF-GCLK[0]/EBI-DATA[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)
unnamed: GCLK1.TP, MCU.68 (PC20/PWM-PWMH[2]/SCIF-GCLK[1]/EBI-DATA[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)
PWM0: JP3.14, MCU.65 (PC17/PWM-PWMH[0]/SPI0-NPCS[2]/EBI-RAS/I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), TP2.TP
PWM1: JP3.12, MCU.63 (PC15/PWM-PWMH[1]/SPI0-NPCS[0]/EBI-SDWE/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), TP1.TP
RXSW: JP3.10, MCU.12 (ADCIN2/AC1AP1/PEVC-PAD_EVT[2]/PA06), TP4.TP
SCK_0: MCU.76 (PD02/SPI0-SCK/TC0-CLK2/EBI-DATA[15]/QDE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), SCK0.TP, SD.CLK
SCK_1: JP5.2, MCU.44 (MACB-RXD[2]/TC0-CLK1/SPI1-SCK/IISC-IMCK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); also elsewhere on the board
SDSW: MCU.81 (PD10/USART1-RI/CANIF-TXLINE[0]/EBI-ADDR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), R119.2, SD.SWB
TPA: JP3.6, MCU.14 (ADCIN4/AC1BP1/EIC-EXTINT[2]/PA08), TP5.TP
TXSW: JP3.8, MCU.13 (ADCIN3/AC1AN1/PEVC-PAD_EVT[3]/PA07), TP3.TP
USART0_RXD: LCD.2, MCU.93 (PD28/USART0-RXD/CANIF-TXLINE[0]/EBI-NCS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)
USART0_TXD: LCD.4, MCU.92 (PD27/USART0-TXD/CANIF-RXLINE[0]/EBI-NCS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)
USART1_CTS: FTDI.3 (RTS#), MCU.86 (PD13/USART1-CTS/USART1-CLK/EBI-SDCK/PEV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)
USART1_RTS: FTDI.11 (CTS#), MCU.87 (PD14/USART1-RTS/EIC-EXTINT[7]/EBI-ADDR[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)
USART1_RXD: FTDI.1 (TXD), MCU.85 (PD12/USART1-RXD/USB-VBOF/EBI-ADDR[9]/PE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)
USART1_TXD: FTDI.5 (RXD), MCU.84 (PD11/USART1-TXD/USB-ID/EBI-ADDR[8]/PEVC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)
VDDANA: CB107.1, CB108.1, FB3.1, MCU.27 (VDDANA), R118.1

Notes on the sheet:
VDDcore
VDDin
VDDIO
ADVREF/VDDANA

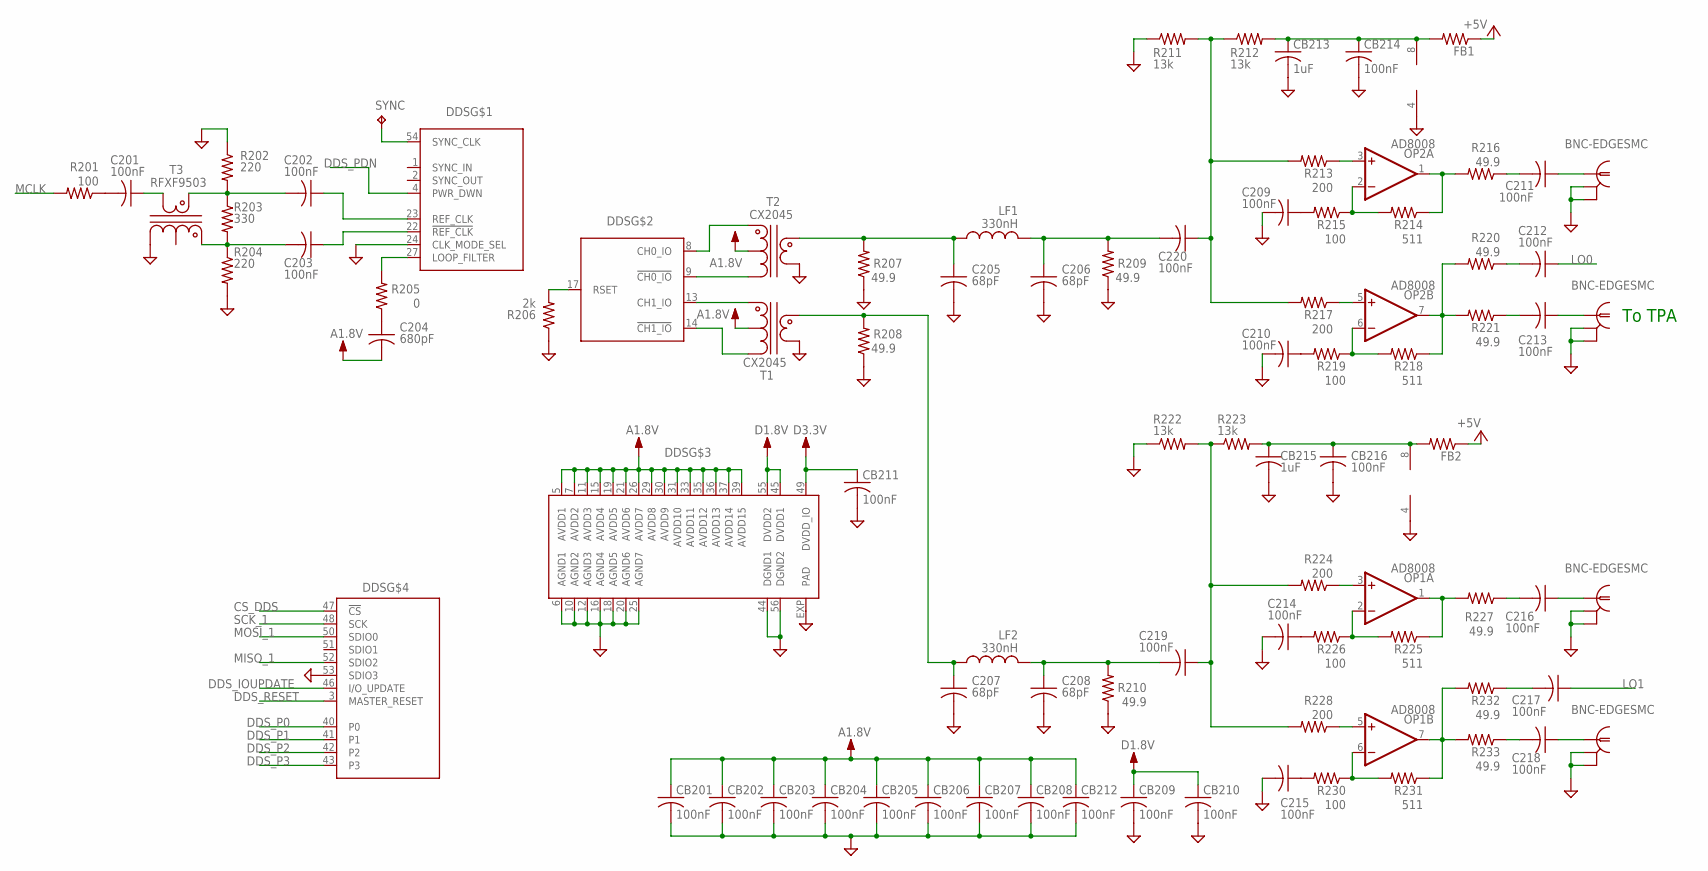
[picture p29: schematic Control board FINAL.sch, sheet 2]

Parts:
C201, C202, C203, C209, C210, C211, C212, C213, C214, C215, C216, C217, C218, C219, C220: 100nF; C0603
C204: 680pF; C0805
C205, C206, C207, C208: 68pF; 1008
CB201, CB202, CB203, CB204, CB205, CB206, CB207, CB208, CB209, CB210, CB211, CB212, CB214, CB216: 100nF; C0603
CB213, CB215: 1uF; C0805
DDS: AD9958; LFCSP-56
FB1, FB2: R-US_R0603; R0603
LF1, LF2: 330nH; 1008
LO0, LO1: BNC-EDGESMC; SMC-EDGE
OP1, OP2: AD8008; SO08
R201, R215, R219, R226, R230: 100; R0805
R202, R204: 220; R0805
R203: 330; R0805
R205: 0; R0805
R206: 2k; R0805
R207, R208, R209, R210, R216, R220, R221, R227, R232, R233: 49.9; R0805
R211, R212, R222, R223: 13k; R0805
R213, R217, R224, R228: 200; R0805
R214, R218, R225, R231: 511; R0805
SYNC: TPTP10R; TP10R
T1, T2: CX2045; CX20XX_BALUN
T3: RFXF9503; CX20XX_BALUN
TX0, TX1: BNC-EDGESMC; SMC-EDGE

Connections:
+5V: FB1.1, FB2.1; also elsewhere on the board
A1.8V: C204.2, CB201.1, CB202.1, CB203.1, CB204.1, CB205.1, CB206.1, CB207.1, CB208.1, CB212.1, DDS.5 (AVDD1), DDS.7 (AVDD2), DDS.11 (AVDD3), DDS.15 (AVDD4), DDS.19 (AVDD5), DDS.21 (AVDD6), DDS.26 (AVDD7), DDS.29 (AVDD8), DDS.30 (AVDD9), DDS.31 (AVDD10), DDS.33 (AVDD11), DDS.35 (AVDD12), DDS.36 (AVDD13), DDS.37 (AVDD14), DDS.39 (AVDD15), T1.P$2 (5), T2.P$2 (5); also elsewhere on the board
A12V1: CB213.1, CB214.1, FB1.2, OP2.8 (V+), R212.2
A12V2: CB215.1, CB216.1, FB2.2, OP1.8 (V+), R223.2
C201: C201.2, R201.1
CS_DDS: DDS.47 (!CS); also elsewhere on the board
D1.8V: CB209.1, CB210.1, DDS.45 (DVDD1), DDS.55 (DVDD2); also elsewhere on the board
D3.3V: CB211.1, DDS.49 (DVDD_IO); also elsewhere on the board
DDS_IOUPDATE: DDS.46 (I/O_UPDATE); also elsewhere on the board
DDS_P0: DDS.40 (P0); also elsewhere on the board
DDS_P1: DDS.41 (P1); also elsewhere on the board
DDS_P2: DDS.42 (P2); also elsewhere on the board
DDS_P3: DDS.43 (P3); also elsewhere on the board
DDS_PDN: DDS.4 (PWR_DWN); also elsewhere on the board
DDS_RESET: DDS.3 (MASTER_RESET); also elsewhere on the board
GND: C205.P$2 (2), C206.P$2 (2), C207.P$2 (2), C208.P$2 (2), C209.2, C210.2, C214.2, C215.2, CB201.2, CB202.2, CB203.2, CB204.2, CB205.2, CB206.2, CB207.2, CB208.2, CB209.2, CB210.2, CB211.2, CB212.2, CB213.2, CB214.2, CB215.2, CB216.2, DDS.6 (AGND1), DDS.10 (AGND2), DDS.12 (AGND3), DDS.16 (AGND4), DDS.18 (AGND5), DDS.20 (AGND6), DDS.24 (CLK_MODE_SEL), DDS.25 (AGND7), DDS.44 (DGND1), DDS.53 (SDIO3), DDS.56 (DGND2), DDS.EXP (PAD), LO0.2 (GND1), LO0.3 (GND2), LO1.2 (GND1), LO1.3 (GND2), OP1.4 (V-), OP2.4 (V-), R202.1, R204.2, R206.1, R207.1, R208.1, R209.1, R210.1, R211.1, R222.1, T1.P$4 (3), T2.P$4 (3), T3.P$3 (4), TX0.2 (GND1), TX0.3 (GND2), TX1.2 (GND1), TX1.3 (GND2); also elsewhere on the board
LO0: C212.1; also elsewhere on the board
LO1: C217.1; also elsewhere on the board
MCLK: R201.2; also elsewhere on the board
MISO_1: DDS.52 (SDIO2); also elsewhere on the board
MOSI_1: DDS.50 (SDIO0); also elsewhere on the board
unnamed: C212.2, R220.1
unnamed: DDS.9 (!CH0_IO), T2.P$3 (4)
unnamed: DDS.8 (CH0_IO), T2.P$1 (6)
unnamed: DDS.14 (!CH1_IO), T1.P$3 (4)
unnamed: DDS.13 (CH1_IO), T1.P$1 (6)
unnamed: C202.1, DDS.23 (REF_CLK)
unnamed: C203.1, DDS.22 (!REF_CLK)
unnamed: C202.2, R202.2, R203.1, T3.P$5 (1)
unnamed: C204.1, R205.1
unnamed: DDS.27 (LOOP_FILTER), R205.2
unnamed: C203.2, R203.2, R204.1, T3.P$1 (6)
unnamed: DDS.17 (RSET), R206.2
unnamed: C217.2, R232.1
unnamed: DDS.54 (SYNC_CLK), SYNC.TP
unnamed: C207.P$1 (1), LF2.P$1 (1), R208.2, T1.P$5 (1)
unnamed: C205.P$1 (1), LF1.P$1 (1), R207.2, T2.P$5 (1)
unnamed: C206.P$1 (1), C220.2, LF1.P$2 (2), R209.2
unnamed: C209.1, R215.2
unnamed: OP2.2 (-IN), R214.2, R215.1
unnamed: OP2.1 (OUT), R214.1, R216.2
unnamed: OP2.3 (+IN), R213.1
unnamed: OP2.6 (-IN), R218.2, R219.1
unnamed: OP2.7 (OUT), R218.1, R220.2, R221.2
unnamed: OP2.5 (+IN), R217.1
unnamed: C210.1, R219.2
unnamed: C208.P$1 (1), C219.2, LF2.P$2 (2), R210.2
unnamed: C211.1, TX0.1
unnamed: C214.1, R226.2
unnamed: OP1.2 (-IN), R225.2, R226.1
unnamed: OP1.1 (OUT), R225.1, R227.2
unnamed: OP1.3 (+IN), R224.1
unnamed: OP1.6 (-IN), R230.1, R231.2
unnamed: OP1.7 (OUT), R231.1, R232.2, R233.2
unnamed: OP1.5 (+IN), R228.1
unnamed: C215.1, R230.2
unnamed: C219.1, R222.2, R223.1, R224.2, R228.2
unnamed: C211.2, R216.1
unnamed: C213.1, LO0.1
unnamed: C213.2, R221.1
unnamed: C216.1, TX1.1
unnamed: C216.2, R227.1
unnamed: C218.1, LO1.1
unnamed: C218.2, R233.1
unnamed: C201.1, T3.P$4 (3)
R211: C220.1, R211.2, R212.1, R213.2, R217.2
SCK_1: DDS.48 (SCK); also elsewhere on the board

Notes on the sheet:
To TPA

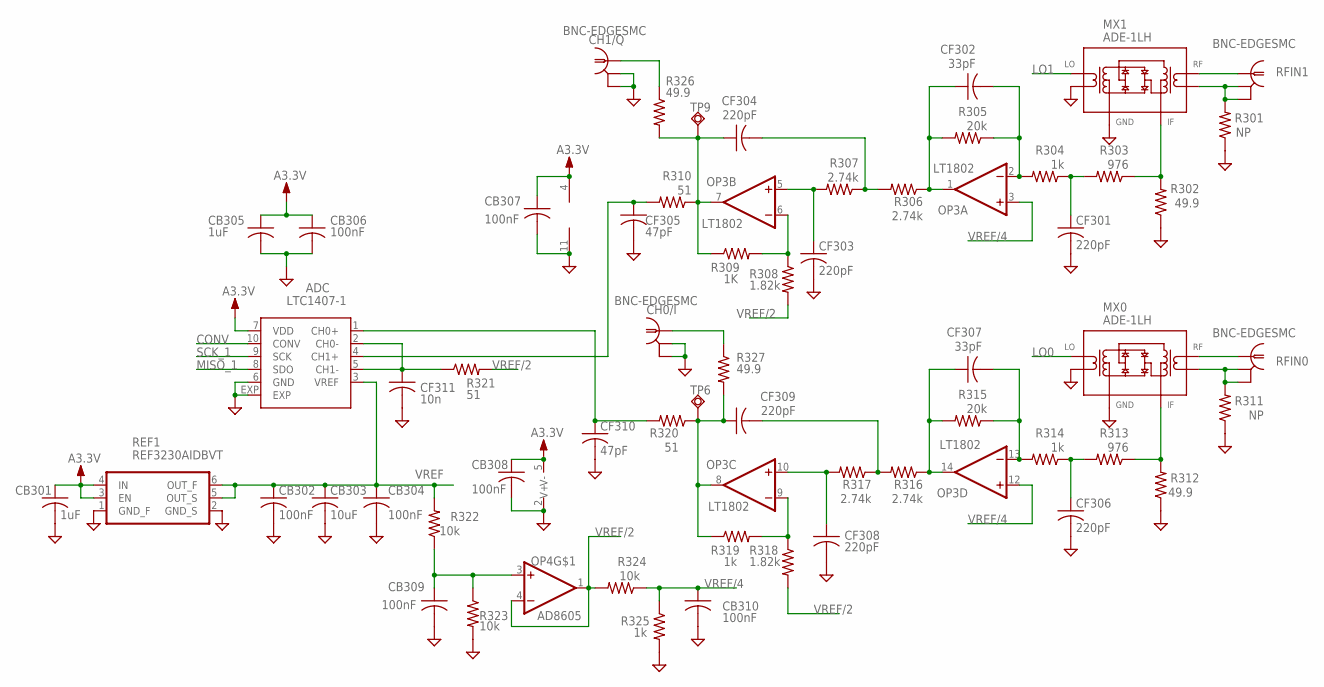
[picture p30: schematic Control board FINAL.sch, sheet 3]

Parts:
ADC: LTC1407-1; MSOP-10-EXP
CB301, CB305: 1uF; C0603
CB302, CB304, CB306, CB307, CB308, CB309, CB310: 100nF; C0603
CB303: 10uF; C0805
CF301, CF303, CF304, CF306, CF308, CF309: 220pF; C0805
CF302, CF307: 33pF; C0805
CF305, CF310: 47pF; C0603
CF311: 10n; C0603
CH0/I, CH1/Q: BNC-EDGESMC; SMC-EDGE
MX0, MX1: ADE-1LH; CD636
OP3: LT1802; SO14
OP4: AD8605; SOT23-5
R301, R311: NP; R0805
R302, R312, R326, R327: 49.9; R0805
R303, R313: 976; R0805
R304, R314, R319, R325: 1k; R0805
R305, R315: 20k; R0805
R306, R307, R316, R317: 2.74k; R0805
R308, R318: 1.82k; R0805
R309: 1K; R0805
R310, R320, R321: 51; R0805
R322, R323, R324: 10k; R0805
REF1: REF3230AIDBVT; SOT23-6
RFIN0, RFIN1: BNC-EDGESMC; SMC-EDGE
TP6, TP9: TPSQTP16R; TP16R

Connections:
A3.3V: ADC.7 (VDD), CB301.1, CB305.1, CB306.1, CB307.1, CB308.1, OP3.4 (V+), OP4.5 (V+), REF1.3 (EN), REF1.4 (IN); also elsewhere on the board
CONV: ADC.10 (CONV); also elsewhere on the board
GND: ADC.6 (GND), ADC.EXP, CB301.2, CB302.2, CB303.2, CB304.2, CB305.2, CB306.2, CB307.2, CB308.2, CB309.2, CB310.2, CF301.2, CF303.2, CF305.2, CF306.2, CF308.2, CF310.2, CF311.2, CH0/I.2 (GND1), CH0/I.3 (GND2), CH1/Q.2 (GND1), CH1/Q.3 (GND2), MX0.P$1 (LON), MX0.P$5 (GND), MX1.P$1 (LON), MX1.P$5 (GND), OP3.11 (V-), OP4.2 (V-), R301.1, R302.1, R311.1, R312.1, R323.2, R325.2, REF1.1 (GND_F), REF1.2 (GND_S); also elsewhere on the board
LO0: MX0.P$6 (LOP); also elsewhere on the board
LO1: MX1.P$6 (LOP); also elsewhere on the board
MISO_1: ADC.8 (SDO); also elsewhere on the board
unnamed: CH0/I.1, R327.1
unnamed: CH1/Q.1, R326.1
unnamed: CF307.2, OP3.13 (-IN), R314.2, R315.1
unnamed: CF309.2, R316.2, R317.1
unnamed: CF308.1, OP3.10 (+IN), R317.2
unnamed: OP3.9 (-IN), R318.1, R319.2
unnamed: ADC.4 (CH1+), CF305.1, R310.2
unnamed: CF307.1, OP3.14 (OUT), R315.2, R316.1
unnamed: CF306.1, R313.2, R314.1
unnamed: MX0.P$2 (IF), R312.2, R313.1
unnamed: CF302.2, OP3.2 (-IN), R304.2, R305.1
unnamed: CF304.2, R306.2, R307.1
unnamed: CF303.1, OP3.5 (+IN), R307.2
unnamed: OP3.6 (-IN), R308.1, R309.2
unnamed: CF304.1, OP3.7 (OUT), R309.1, R310.1, R326.2, TP9.TP
unnamed: CF302.1, OP3.1 (OUT), R305.2, R306.1
unnamed: CF301.1, R303.2, R304.1
unnamed: MX1.P$2 (IF), R302.2, R303.1
unnamed: MX1.P$3 (RFP), RFIN1.1
unnamed: MX0.P$3 (RFP), RFIN0.1
unnamed: ADC.2 (CH0-), ADC.5 (CH1-), CF311.1, R321.1
unnamed: CB309.1, OP4.3 (+IN), R322.1, R323.1
unnamed: CF309.1, OP3.8 (OUT), R319.1, R320.1, R327.2, TP6.TP
unnamed: ADC.1 (CH0+), CF310.1, R320.2
unnamed: MX0.P$4 (RFN), R311.2, RFIN0.2 (GND1), RFIN0.3 (GND2)
unnamed: MX1.P$4 (RFN), R301.2, RFIN1.2 (GND1), RFIN1.3 (GND2)
SCK_1: ADC.9 (SCK); also elsewhere on the board
VREF: ADC.3 (VREF), CB302.1, CB303.1, CB304.1, R322.2, REF1.5 (OUT_S), REF1.6 (OUT_F)
VREF/2: OP4.1 (OUT), OP4.4 (-IN), R308.2, R318.2, R321.2, R324.2
VREF/4: CB310.1, OP3.3 (+IN), OP3.12 (+IN), R324.1, R325.1

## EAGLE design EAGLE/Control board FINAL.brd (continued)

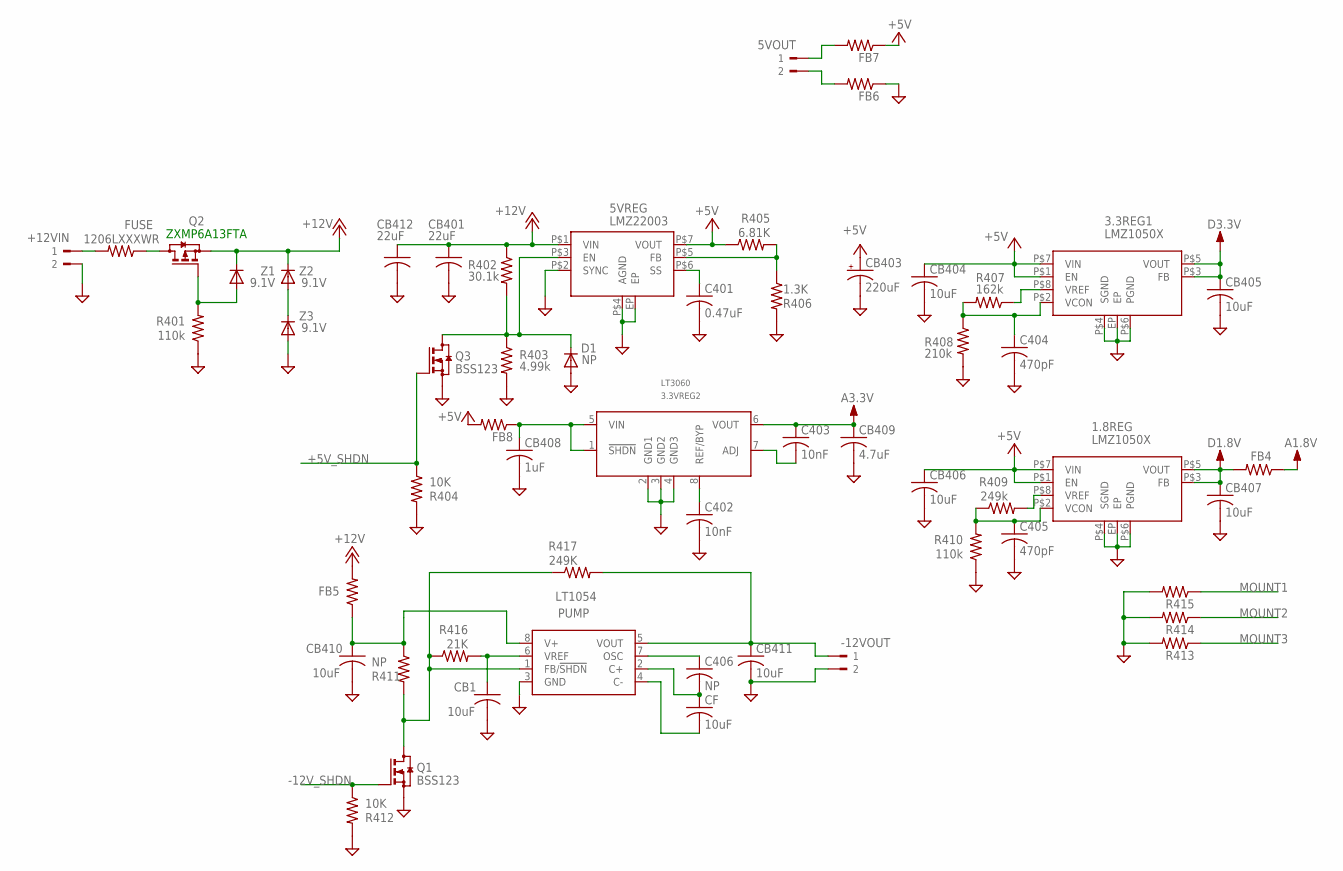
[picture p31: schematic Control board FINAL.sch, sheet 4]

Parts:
1.8REG, 3.3REG1: LMZ1050X; LLP-8
3.3VREG2: LT3060; TSOT-8
5VOUT: TERM-2OMNIMATE_SL; OMNIMATE_SL_2POS
5VREG: LMZ22003; TO-PMOD7
+12VIN: TERM-2OMNIMATE_SL; OMNIMATE_SL_2POS
-12VOUT: TERM-2OMNIMATE_SL; OMNIMATE_SL_2POS
C401: 0.47uF; C0805
C402, C403: 10nF; C0603
C404, C405: 470pF; C0603
C406: NP; C0805
CB1, CB404, CB405, CB406, CB407, CB410, CB411: 10uF; C0805
CB401, CB412: 22uF; C1210
CB403: 220uF; E3,5-8
CB408: 1uF; C0805
CB409: 4.7uF; C0805
CF: 10uF; C0805
D1: NP; SOD323-W
FB4: R-US_R0805; R0805
FB5, FB6, FB7, FB8: R-US_R0603; R0603
FUSE: 1206LXXXWR; R1206
PUMP: LT1054; SOIC-8
Q1, Q3: BSS123; SOT23
Q2: ZXMP6A13FTA; SOT23
R401, R410: 110k; R0805
R402: 30.1k; R0805
R403: 4.99k; R0805
R404, R412: 10K; R0805
R405: 6.81K; R0805
R406: 1.3K; R0805
R407: 162k; R0805
R408: 210k; R0805
R409: 249k; R0805
R411: NP; R0805
R413, R414, R415: R-US_R0805; R0805
R416: 21K; R0805
R417: 249K; R0805
Z1: 9.1V; SOD123
Z2, Z3: 9.1V; DO214AC

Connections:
+5V: 1.8REG.P$1 (EN), 1.8REG.P$7 (VIN), 3.3REG1.P$1 (EN), 3.3REG1.P$7 (VIN), 5VREG.P$7 (VOUT), CB403.+, CB404.1, CB406.1, FB7.1, FB8.2, R405.1; also elsewhere on the board
+5V_SHDN: Q3.1 (G), R404.1; also elsewhere on the board
+12V: 5VREG.P$1 (VIN), CB401.1, CB412.1, FB5.2, Q2.2 (S), R402.1, Z1.C, Z2.C
-12V_SHDN: Q1.1 (G), R412.1; also elsewhere on the board
A1.8V: FB4.1; also elsewhere on the board
A3.3V: 3.3VREG2.6 (VOUT), C403.1, CB409.1; also elsewhere on the board
D1.8V: 1.8REG.P$3 (FB), 1.8REG.P$5 (VOUT), CB407.1, FB4.2; also elsewhere on the board
D3.3V: 3.3REG1.P$3 (FB), 3.3REG1.P$5 (VOUT), CB405.1; also elsewhere on the board
GND: 1.8REG.EP, 1.8REG.P$4 (SGND), 1.8REG.P$6 (PGND), 3.3REG1.EP, 3.3REG1.P$4 (SGND), 3.3REG1.P$6 (PGND), 3.3VREG2.2 (GND1), 3.3VREG2.3 (GND2), 3.3VREG2.4 (GND3), 5VREG.EP, 5VREG.P$2 (SYNC), 5VREG.P$4 (AGND), +12VIN.2, -12VOUT.2, C401.2, C402.2, C404.2, C405.2, CB1.2, CB401.2, CB403.-, CB404.2, CB405.2, CB406.2, CB407.2, CB408.2, CB409.2, CB410.2, CB411.2, CB412.2, D1.A, FB6.1, PUMP.3 (GND), Q1.2 (S), Q3.2 (S), R401.1, R403.2, R404.2, R406.2, R408.2, R410.1, R412.2, R413.2, R414.2, R415.2, Z3.A; also elsewhere on the board
MOUNT1: R415.1
MOUNT2: R414.1
MOUNT3: R413.1
unnamed: 5VREG.P$6 (SS), C401.1
unnamed: 5VREG.P$3 (EN), D1.C, Q3.3 (D), R402.2, R403.1
unnamed: 5VOUT.1, FB7.2
unnamed: 5VOUT.2, FB6.2
unnamed: C406.1, PUMP.7 (OSC)
unnamed: C406.2, CF.1, PUMP.2 (C+)
unnamed: 5VREG.P$5 (FB), R405.2, R406.1
unnamed: CB410.1, FB5.1, PUMP.8 (V+), R411.1
unnamed: 3.3REG1.P$2 (VCON), C404.1, R407.2, R408.1
unnamed: 3.3REG1.P$8 (VREF), R407.1
unnamed: 1.8REG.P$8 (VREF), R409.2
unnamed: 1.8REG.P$2 (VCON), C405.1, R409.1, R410.2
unnamed: CB1.1, PUMP.6 (VREF), R416.2
unnamed: 3.3VREG2.8 (REF/BYP), C402.1
unnamed: 3.3VREG2.7 (ADJ), C403.2
unnamed: +12VIN.1, FUSE.2
unnamed: Q2.1 (G), R401.2, Z1.A
unnamed: FUSE.1, Q2.3 (D)
unnamed: -12VOUT.1, CB411.1, PUMP.5 (VOUT), R417.2
unnamed: CF.2, PUMP.4 (C-)
unnamed: Z2.A, Z3.C
unnamed: 3.3VREG2.1 (!SHDN), 3.3VREG2.5 (VIN), CB408.1, FB8.1
unnamed: PUMP.1 (FB/!SHDN), Q1.3 (D), R411.2, R416.1, R417.1

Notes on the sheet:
ZXMP6A13FTA

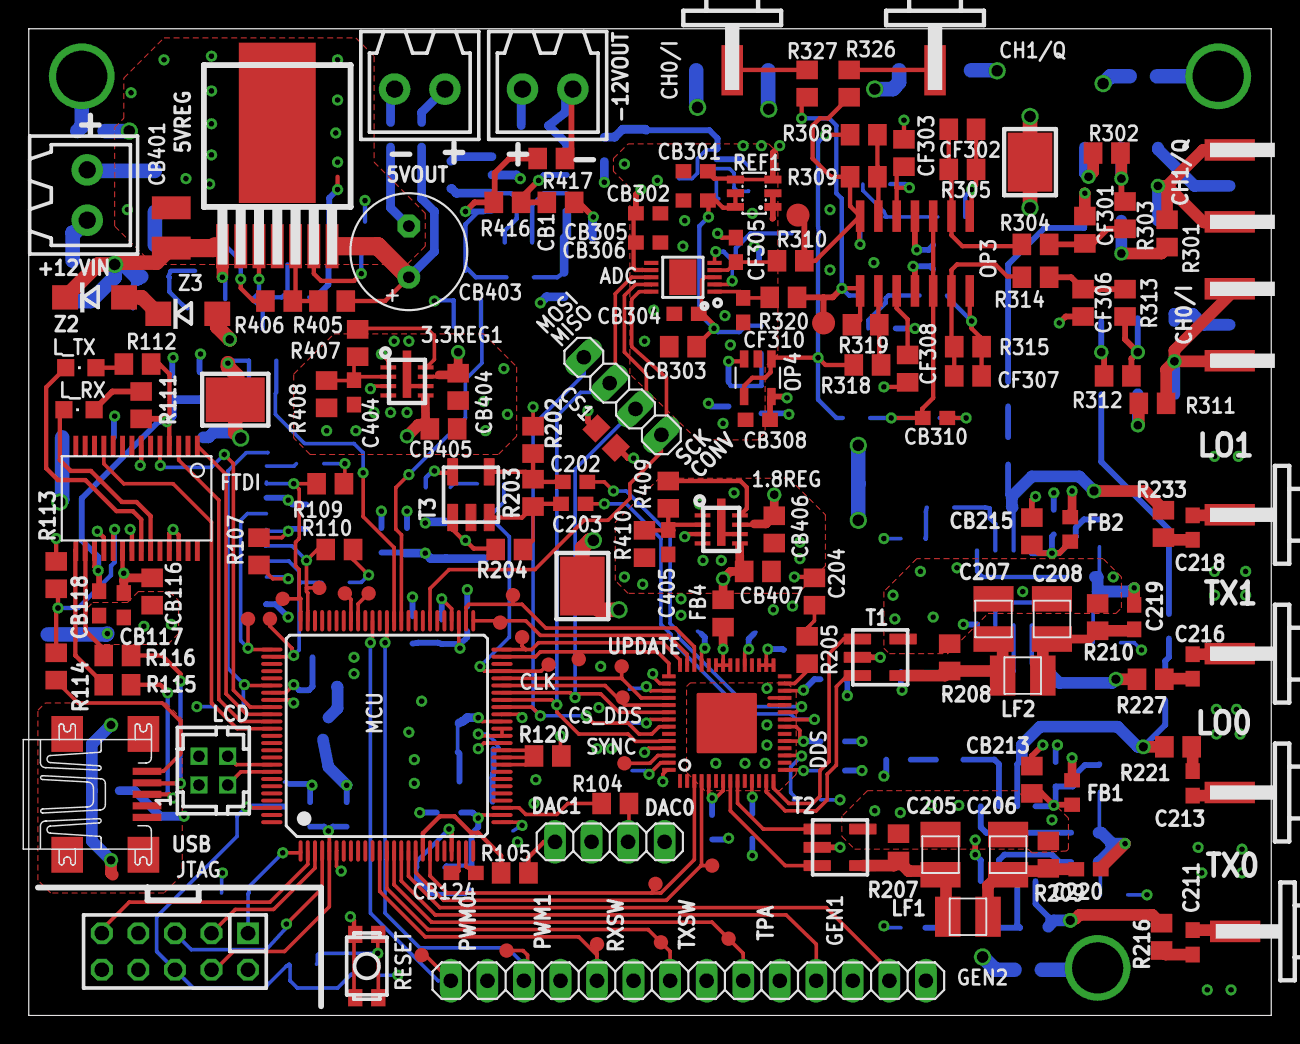
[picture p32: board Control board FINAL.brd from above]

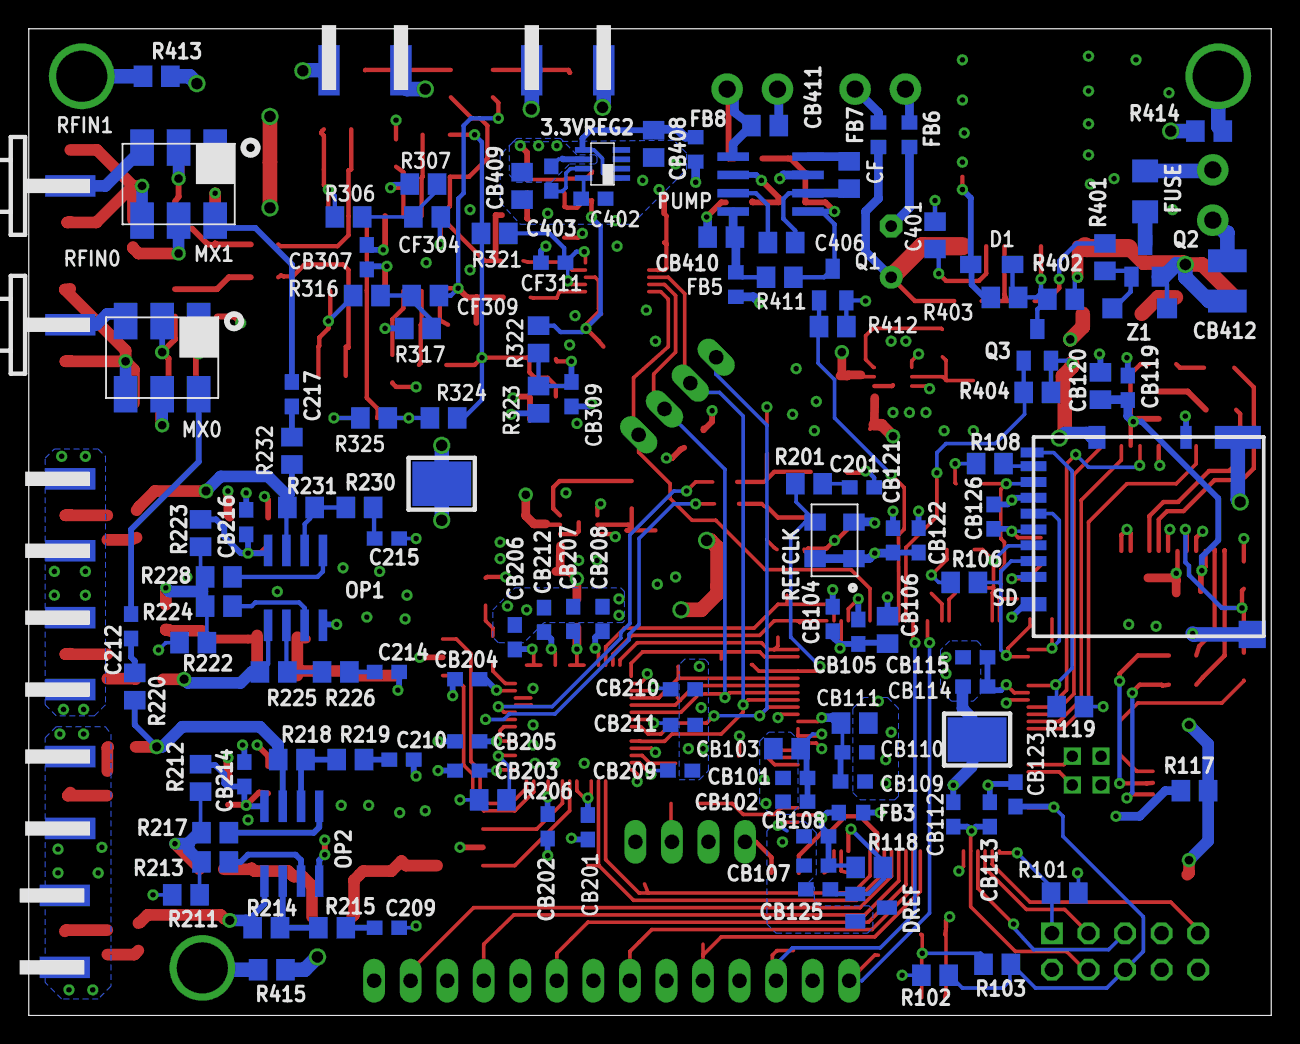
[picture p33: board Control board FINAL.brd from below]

Board: 4 copper layers, 86.4 x 68.6 mm, 287 parts (128 on the bottom side), 174 nets.

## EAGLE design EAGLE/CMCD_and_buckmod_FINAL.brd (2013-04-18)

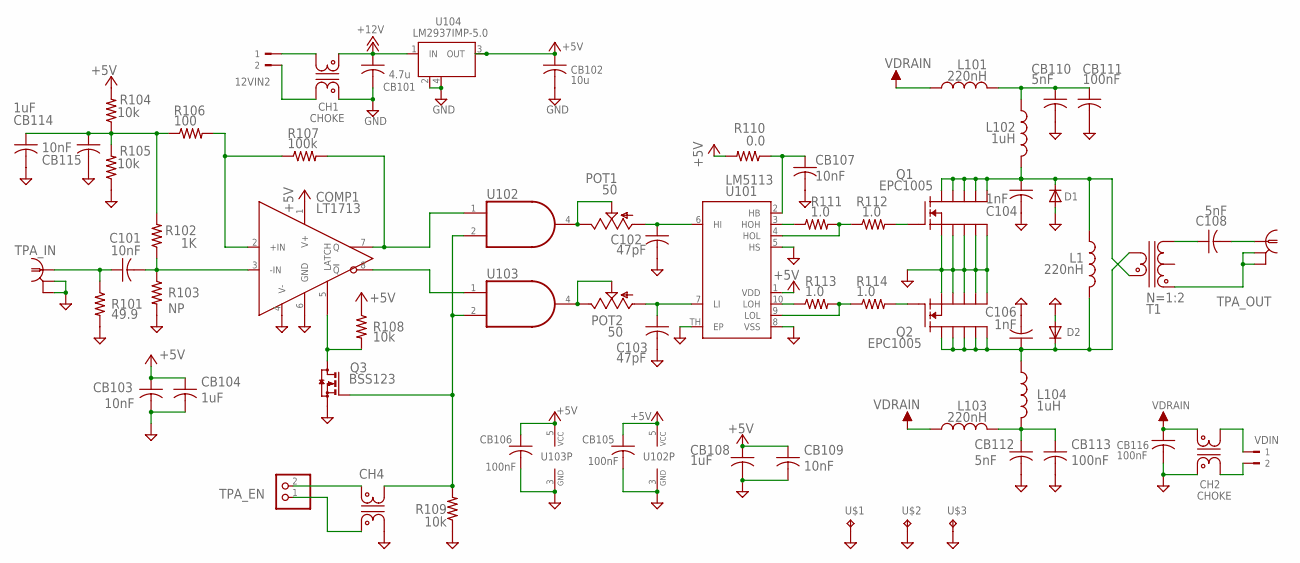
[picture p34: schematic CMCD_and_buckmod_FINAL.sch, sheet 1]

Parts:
12VIN2: TERM-2OMNIMATE_SL; OMNIMATE_SL_2POS
C101: 10nF; C0805
C102, C103: 47pF; C0805
C104, C106: 1nF; 1008
C108: 5nF; 1008
CB101: 4.7u; C0805
CB102: 10u; C0805
CB103, CB107, CB109, CB115: 10nF; C0603
CB104, CB108: 1uF; C0603
CB105, CB106: 100nF; C0603
CB110, CB112: 5nF; 1008
CB111, CB113, CB116: 100nF; C0805
CB114: 1uF; C0805
CH1, CH2: CHOKE; CHOKE_DLW5BT
CH4: CHOKEDLW31S; CHOKE_DLW31S
COMP1: LT1713; MSOP-8
D1, D2: DIODE-DO214AC; DO214AC
L1, L101, L103: 220nH; GENERAL-1
L102, L104: 1uH; GENERAL-1
POT1, POT2: 50; 3223W
Q1, Q2: EPC1005; 11-LGA
Q3: BSS123; SOT23
R101: 49.9; R0805
R102: 1K; R0805
R103: NP; R0805
R104, R105, R108, R109: 10k; R0805
R106: 100; R0805
R107: 100k; R0805
R110: 0.0; R0603
R111, R112, R113, R114: 1.0; R0603
T1: N=1:2; BALUN_GENERAL_BIG
TPA_EN: PINHD-1X2; 1X02
TPA_IN: BNC-EDGE
TPA_OUT: BNC-EDGE
U101: LM5113; LLP-10
U102, U103: 74AHC1G08DBV; SOT23-5
U104: LM2937IMP-5.0; SOT223
U$1, U$2, U$3: TESTPOINTKEYSTONE_ELECTRONICS_5016; SMD_TESTPAD
VDIN: TERM-2OMNIMATE_SL; OMNIMATE_SL_2POS

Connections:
+5V: CB102.1, CB103.1, CB104.1, CB105.1, CB106.1, CB108.1, CB109.1, COMP1.1 (V+), R104.2, R108.1, R110.2, U101.1 (VDD), U102.5 (VCC), U103.5 (VCC), U104.3 (OUT); also elsewhere on the board
+12V: CB101.1, CH1.P$4 (4), U104.1 (IN); also elsewhere on the board
GND: C102.2, C103.2, C104.P$2 (2), C106.P$2 (2), CB101.2, CB102.2, CB103.2, CB104.2, CB105.2, CB106.2, CB107.2, CB108.2, CB109.2, CB110.P$2 (2), CB111.2, CB112.P$2 (2), CB113.2, CB114.2, CB115.2, CB116.2, CH1.P$1 (1), CH2.P$1 (1), CH4.P$2 (2), COMP1.4 (V-), COMP1.6 (GND), D1.A, D2.A, Q1.2 (S1), Q1.4 (S2), Q1.6 (S3), Q1.8 (S4), Q1.10 (S5), Q2.2 (S1), Q2.4 (S2), Q2.6 (S3), Q2.8 (S4), Q2.10 (S5), Q3.2 (S), R101.2, R103.2, R105.1, R109.1, TPA_IN.S1 (GND1), TPA_IN.S2 (GND2), U101.5 (HS), U101.8 (VSS), U101.TH (EP), U102.3 (GND), U103.3 (GND), U104.2 (GND), U104.4 (GND), U$1.P$1, U$2.P$1, U$3.P$1; also elsewhere on the board
unnamed: R111.1, U101.3 (HOH)
unnamed: R111.2, R112.1, U101.4 (HOL)
unnamed: R113.1, U101.10 (LOH)
unnamed: R113.2, R114.1, U101.9 (LOL)
unnamed: Q2.1 (G), R114.2
unnamed: Q1.1 (G), R112.2
unnamed: CB107.1, R110.1, U101.2 (HB)
unnamed: COMP1.7 (Q), R107.2, U102.1 (I0)
unnamed: POT1.2 (S), POT1.3 (E), U102.4 (O)
unnamed: POT2.2 (S), POT2.3 (E), U103.4 (O)
unnamed: CB114.1, CB115.1, R102.2, R104.1, R105.2, R106.1
unnamed: COMP1.8 (!Q), U103.1 (I0)
unnamed: COMP1.5 (LATCH), Q3.3 (D), R108.2
unnamed: T1.S1 (6), TPA_OUT.S1 (GND1), TPA_OUT.S2 (GND2)
unnamed: C102.1, POT1.1 (A), U101.6 (HI)
unnamed: COMP1.2 (+IN), R106.2, R107.1
unnamed: C101.2, COMP1.3 (-IN), R102.1, R103.1
unnamed: C101.1, R101.1, TPA_IN.I (1)
unnamed: CH4.P$3 (3), Q3.1 (G), R109.2, U102.2 (I1), U103.2 (I1)
unnamed: CH2.P$3 (3), VDIN.1
unnamed: CH2.P$2 (2), VDIN.2
unnamed: C106.P$1 (1), D2.C, L1.P$2 (2), L104.P$1 (1), Q2.3 (D1), Q2.5 (D2), Q2.7 (D3), Q2.9 (D4), Q2.11 (D5), T1.P2 (3)
unnamed: C103.1, POT2.1 (A), U101.7 (LI)
unnamed: C104.P$1 (1), D1.C, L1.P$1 (1), L102.P$2 (2), Q1.3 (D1), Q1.5 (D2), Q1.7 (D3), Q1.9 (D4), Q1.11 (D5), T1.P1 (1)
unnamed: CB110.P$1 (1), CB111.1, L101.P$2 (2), L102.P$1 (1)
unnamed: CB112.P$1 (1), CB113.1, L103.P$2 (2), L104.P$2 (2)
unnamed: C108.P$2 (2), TPA_OUT.I (1)
unnamed: C108.P$1 (1), T1.S2 (4)
unnamed: 12VIN2.1, CH1.P$3 (3)
unnamed: 12VIN2.2, CH1.P$2 (2)
unnamed: CH4.P$4 (4), TPA_EN.2
unnamed: CH4.P$1 (1), TPA_EN.1
VDRAIN: CB116.1, CH2.P$4 (4), L101.P$1 (1), L103.P$1 (1)

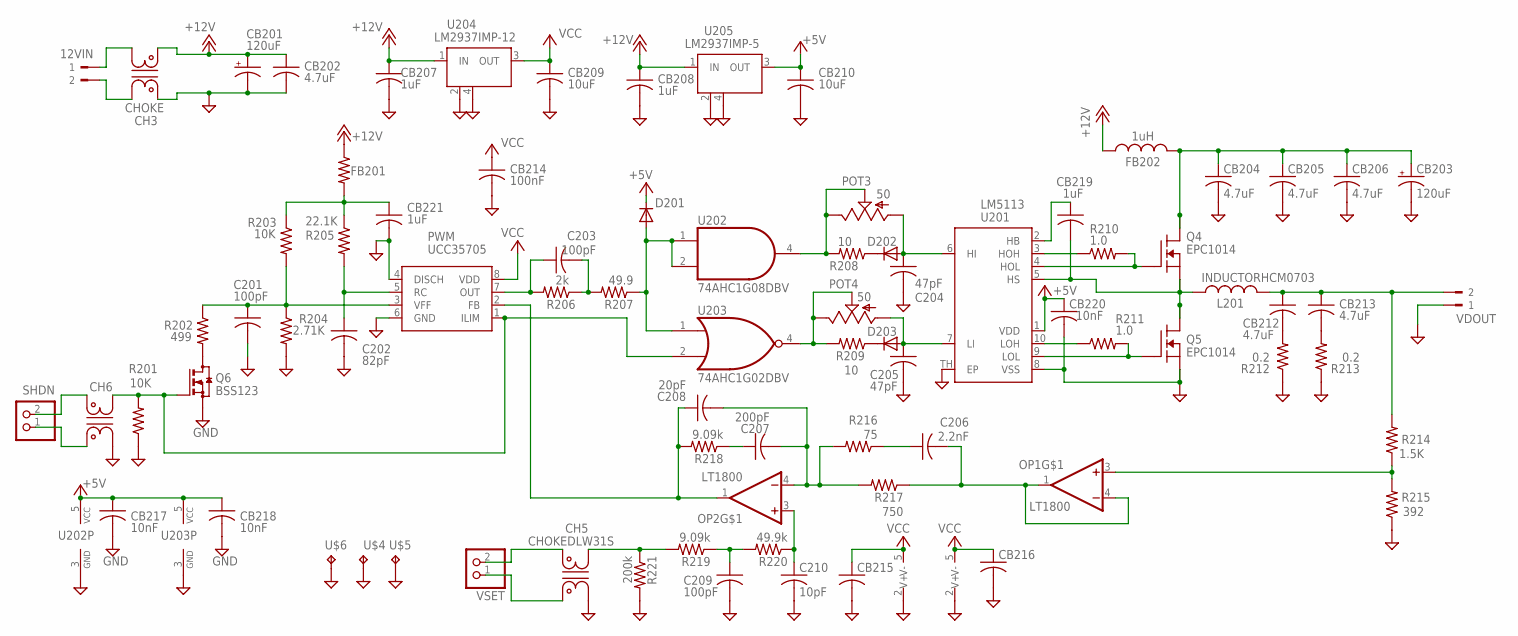
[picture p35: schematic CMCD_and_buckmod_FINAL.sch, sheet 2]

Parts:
12VIN: TERM-2OMNIMATE_SL; OMNIMATE_SL_2POS
C201, C203, C209: 100pF; C0805
C202: 82pF; C0805
C204, C205: 47pF; C0603
C206: 2.2nF; C0805
C207: 200pF; C0805
C208: 20pF; C0805
C210: 10pF; C0805
CB201, CB203: 120uF; E3,5-8
CB202, CB204, CB212, CB213: 4.7uF; C0805
CB205, CB206: 4.7uF; 1206-LONG
CB207, CB208, CB221: 1uF; C0805
CB209, CB210: 10uF; C0805
CB214: 100nF; C0603
CB215, CB216: C-USC0603; C0603
CB217, CB218, CB220: 10nF; C0603
CB219: 1uF; C0603
CH3: CHOKE; CHOKE_DLW5BT
CH5, CH6: CHOKEDLW31S; CHOKE_DLW31S
D201, D202, D203: DIODE-SOD323-W; SOD323-W
FB201: R-US_R0805; R0805
FB202: 1uH; 1008
L201: INDUCTORHCM0703; HCM0703
OP1, OP2: LT1800; SOT23-5
POT3, POT4: 50; 3223W
PWM: UCC35705; MSOP-8
Q4, Q5: EPC1014; 5-LGA
Q6: BSS123; SOT23
R201, R203: 10K; R0805
R202: 499; R0805
R204: 2.71K; R0805
R205: 22.1K; R0805
R206: 2k; R0805
R207: 49.9; R0805
R208, R209: 10; R0805
R210, R211: 1.0; R0603
R212, R213: 0.2; R0805
R214: 1.5K; R0805
R215: 392; R0805
R216: 75; R0805
R217: 750; R0805
R218, R219: 9.09k; R0805
R220: 49.9k; R0805
R221: 200k; R0805
SHDN: PINHD-1X2; 1X02
U201: LM5113; LLP-10
U202: 74AHC1G08DBV; SOT23-5
U203: 74AHC1G02DBV; SOT23-5
U204: LM2937IMP-12; SOT223
U205: LM2937IMP-5; SOT223
U$4, U$5, U$6: TESTPOINTKEYSTONE_ELECTRONICS_5016; SMD_TESTPAD
VDOUT: TERM-2OMNIMATE_SL; OMNIMATE_SL_2POS
VSET: PINHD-1X2; 1X02

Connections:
+5V: CB210.1, CB217.1, CB218.1, CB220.1, D201.C, U201.1 (VDD), U202.5 (VCC), U203.5 (VCC), U205.3 (OUT); also elsewhere on the board
+12V: CB201.+, CB202.1, CB207.1, CB208.1, CH3.P$4 (4), FB201.1, FB202.P$1 (1), U204.1 (IN), U205.1 (IN); also elsewhere on the board
+VIN: CB203.+, CB204.1, CB205.1, CB206.1, FB202.P$2 (2), Q4.3 (D), Q4.5 (D1)
GND: C201.2, C202.2, C204.2, C205.2, C209.2, C210.2, CB201.-, CB202.2, CB203.-, CB204.2, CB205.2, CB206.2, CB207.2, CB208.2, CB209.2, CB210.2, CB214.2, CB215.2, CB216.2, CB217.2, CB218.2, CB220.2, CB221.2, CH3.P$1 (1), CH5.P$2 (2), CH6.P$2 (2), OP1.2 (V-), OP2.2 (V-), PWM.4 (DISCH), PWM.6 (GND), Q5.2 (S1), Q5.4 (S2), Q6.2 (S), R201.1, R204.2, R212.1, R213.1, R215.1, R221.2, U201.8 (VSS), U201.TH (EP), U202.3 (GND), U203.3 (GND), U204.2 (GND), U204.4 (GND), U205.2 (GND), U205.4 (GND), U$4.P$1, U$5.P$1, U$6.P$1, VDOUT.1; also elsewhere on the board
unnamed: 12VIN.2, CH3.P$2 (2)
unnamed: 12VIN.1, CH3.P$3 (3)
unnamed: R210.1, U201.3 (HOH)
unnamed: Q4.1 (G), R210.2, U201.4 (HOL)
unnamed: CH5.P$4 (4), VSET.2
unnamed: CH5.P$1 (1), VSET.1
unnamed: CH6.P$4 (4), SHDN.2
unnamed: CH6.P$1 (1), SHDN.1
unnamed: R211.1, U201.10 (LOH)
unnamed: Q5.1 (G), R211.2, U201.9 (LOL)
unnamed: CB219.2, L201.P$1 (1), Q4.2 (S1), Q4.4 (S2), Q5.3 (D), Q5.5 (D1), U201.5 (HS)
unnamed: C205.1, D203.A, POT4.1 (A), U201.7 (LI)
unnamed: C204.1, D202.A, POT3.1 (A), U201.6 (HI)
unnamed: POT4.2 (S), POT4.3 (E), R209.2, U203.4 (O)
unnamed: CB219.1, U201.2 (HB)
unnamed: C208.1, OP2.1 (OUT), PWM.2 (FB), R218.2
unnamed: C207.2, C208.2, OP2.4 (-IN), R216.2, R217.2
unnamed: C207.1, R218.1
unnamed: C206.1, R216.1
unnamed: C206.2, OP1.1 (OUT), OP1.4 (-IN), R217.1
unnamed: CB213.2, R213.2
unnamed: CB212.1, CB213.1, L201.P$2 (2), R214.2, VDOUT.2
unnamed: OP1.3 (+IN), R214.1, R215.2
unnamed: C209.1, R219.1, R220.2
unnamed: CB212.2, R212.2
unnamed: CH5.P$3 (3), R219.2, R221.1
unnamed: D201.A, R207.1, U202.1 (I0), U202.2 (I1), U203.1 (I0)
unnamed: C202.1, PWM.5 (RC), R205.2
unnamed: C201.1, PWM.3 (VFF), R202.1, R203.2, R204.1
unnamed: C203.1, PWM.7 (OUT), R206.2
unnamed: C203.2, R206.1, R207.2
unnamed: Q6.3 (D), R202.2
unnamed: CB221.1, FB201.2, R203.1, R205.1
unnamed: D203.C, R209.1
unnamed: D202.C, R208.1
unnamed: POT3.2 (S), POT3.3 (E), R208.2, U202.4 (O)
unnamed: CH6.P$3 (3), PWM.1 (ILIM), Q6.1 (G), R201.2, U203.2 (I1)
OP2: C210.1, OP2.3 (+IN), R220.1
VCC: CB209.1, CB214.1, CB215.1, CB216.1, OP1.5 (V+), OP2.5 (V+), PWM.8 (VDD), U204.3 (OUT)



Board: 4 copper layers, 77.5 x 81.3 mm, 145 parts (33 on the bottom side), 76 nets.

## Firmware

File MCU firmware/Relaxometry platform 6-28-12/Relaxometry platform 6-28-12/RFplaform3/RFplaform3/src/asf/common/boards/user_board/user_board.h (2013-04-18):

/**
 * \file
 *
 * \brief User board definition template
 *
 */

#  define USB_USART                 (&AVR32_USART1)			//USB USART assignments third version of RF platform
#  define USB_USART_TX_PDCA_PID		AVR32_PDCA_PID_USART1_TX
#  define USB_USART_RX_PDCA_PID		AVR32_PDCA_PID_USART1_RX
#  define USB_USART_RX_PIN          AVR32_USART1_RXD_0_1_PIN	//PD12
#  define USB_USART_RX_FUNCTION     AVR32_USART1_RXD_0_1_FUNCTION	//
#  define USB_USART_TX_PIN          AVR32_USART1_TXD_0_1_PIN		//PD11
#  define USB_USART_TX_FUNCTION     AVR32_USART1_TXD_0_1_FUNCTION	//
#  define USB_USART_CTS_PIN          AVR32_USART1_CTS_0_1_PIN		//PD11
#  define USB_USART_CTS_FUNCTION     AVR32_USART1_CTS_0_1_FUNCTION	//
#  define USB_USART_RTS_PIN          AVR32_USART1_RTS_0_1_PIN		//PD11
#  define USB_USART_RTS_FUNCTION     AVR32_USART1_RTS_0_1_FUNCTION	//

#  define LCD_USART                 (&AVR32_USART0)			//USART for communicating with LCD
#  define LCD_USART_RX_PDCA_PID		AVR32_PDCA_PID_USART0_RX
#  define LCD_USART_RX_PIN          AVR32_USART0_RXD_0_0_PIN	//PD28
#  define LCD_USART_RX_FUNCTION     AVR32_USART0_RXD_0_0_FUNCTION  //
#  define LCD_USART_TX_PIN          AVR32_USART0_TXD_0_0_PIN		//PD27
#  define LCD_USART_TX_FUNCTION     AVR32_USART0_TXD_0_0_FUNCTION	//

#  define SPI1					    (&AVR32_SPI1)				//THESE ARE SPI ASSIGNMENTS FOR EVK HACK
#  define SPI1_RX_PDCA_PID				AVR32_PDCA_PID_SPI1_RX
#  define SPI1_NPCS2_PIN				AVR32_SPI1_NPCS_3_2_PIN 		//PAB23 is DDS CS
#  define SPI1_NPCS2_FUNCTION			AVR32_SPI1_NPCS_3_2_FUNCTION
#  define SPI1_MISO_PIN				AVR32_SPI1_MISO_0_1_PIN		//PB20
#  define SPI1_MISO_FUNCTION			AVR32_SPI1_MISO_0_1_FUNCTION
#  define SPI1_MOSI_PIN				AVR32_SPI1_MOSI_0_1_PIN		//PB19
#  define SPI1_MOSI_FUNCTION			AVR32_SPI1_MOSI_0_1_FUNCTION
#  define SPI1_SCK_PIN				AVR32_SPI1_SCK_0_1_PIN 		//PB21
#  define SPI1_SCK_FUNCTION			AVR32_SPI1_SCK_0_1_FUNCTION

#  define SPI0						   (&AVR32_SPI0)				//THESE ARE SPI ASSIGNMENTS FOR EVK HACK
#  define SPI0_TX_PDCA_PID			AVR32_PDCA_PID_SPI0_TX
#  define SPI0_RX_PDCA_PID			AVR32_PDCA_PID_SPI0_RX
#  define SD_MMC_SPI					(&AVR32_SPI0)
#  define SD_MMC_SPI_NPCS				0
#  define SPI0_RX_PDCA_PID				AVR32_PDCA_PID_SPI0_RX
#  define SPI0_NPCS0_PIN				AVR32_SPI0_NPCS_0_0_PIN		//PD03 is NPCS0, CS for SD card
#  define SPI0_NPCS0_FUNCTION			AVR32_SPI0_NPCS_0_0_FUNCTION
#  define SPI0_MISO_PIN				AVR32_SPI0_MISO_0_0_PIN		//PD01
#  define SPI0_MISO_FUNCTION			AVR32_SPI0_MISO_0_0_FUNCTION
#  define SPI0_MOSI_PIN				AVR32_SPI0_MOSI_0_0_PIN  	//PD00
#  define SPI0_MOSI_FUNCTION			AVR32_SPI0_MOSI_0_0_FUNCTION
#  define SPI0_SCK_PIN				AVR32_SPI0_SCK_0_0_PIN 		//PD02
#  define SPI0_SCK_FUNCTION			AVR32_SPI0_SCK_0_0_FUNCTION

//GPIO assignments for RF platform 3
#  define ADC_CONV_pin					AVR32_PIN_PC06	
#  define DDS_IOUD_pin					AVR32_PIN_PB23
#  define DDS_RESET_pin					AVR32_PIN_PA13
#  define DDS_PDN_pin					AVR32_PIN_PA11
#  define DDS_P0_pin					AVR32_PIN_PC03
#  define DDS_P1_pin					AVR32_PIN_PC02
#  define DDS_P2_pin					AVR32_PIN_PC01
#  define DDS_P3_pin					AVR32_PIN_PC00

#  define TPAbias_pin					AVR32_PIN_PA08
#  define TXSW_pin						AVR32_PIN_PA07
#  define RXSW_pin						AVR32_PIN_PA06
#  define PWM0_pin						AVR32_PIN_PC17
#  define PWM1_pin						AVR32_PIN_PC15
#  define GEN1_pin						AVR32_PIN_PA09
#  define GEN2_pin						AVR32_PIN_PA10
#  define SD_detect_pin					AVR32_PIN_PD10

#  define DAC0					(&AVR32_DACIFB0)
#  define DAC1					(&AVR32_DACIFB1)
#  define DAC0A_pin				AVR32_DAC0A_PIN  	//PD00
#  define DAC0A_FUNCTION			AVR32_DAC0A_FUNCTION
#  define DAC1A_pin				AVR32_DAC1A_PIN  	//PD00
#  define DAC1A_FUNCTION			AVR32_DAC1A_FUNCTION

# define DAC_PRESCALER_CLK	7500000

#define DDS_PCS 7
#define ADC_PCS 14

#define FAST_TC				(&AVR32_TC0)
#define FAST_TC_CHANNEL		0
#define SLOW_TC				(&AVR32_TC1)
#define SLOW_TC_fast_CHANNEL		1
#define SLOW_TC_slow_CHANNEL		0

#define TC1_TCIOA1_pin			AVR32_PIN_PB02

#define OSC0_STARTUP    0	//for external oscillator
#define FOSC0       20000000
#define CPU_SPEED   60000000
#define PBA_SPEED   60000000

#define desired_DDS_Fs 300000000
#if (desired_DDS_Fs>500000000 || (desired_DDS_Fs>160000000 && desired_DDS_Fs < 255000000))
#error "Specified Fs is out of range"
#endif

#define DDS_PLL_div (desired_DDS_Fs/FOSC0)
#if (DDS_PLL_div<4 || DDS_PLL_div>20)
#error "DDS PLL multiplication factor out of range"
#endif

#define DDS_Fs (FOSC0*DDS_PLL_div)
#if (DDS_Fs>500000000 || (DDS_Fs>160000000 && DDS_Fs < 255000000))
#error "Actual Fs is out of range"
#endif

#if DDS_Fs<=160000000
#define DDS_VCO_gain 0
#else
#define DDS_VCO_gain 1
#endif

#define SD_SPI_SPEED 20000000
#define DDS_SPI		(&AVR32_SPI1)

#define SPI1_RX_PDCA_CHANNEL 0
#define SPI0_RX_PDCA_CHANNEL 1
#define SPI0_TX_PDCA_CHANNEL 2
#define USB_USART_TX_PDCA_CHANNEL 3
#define USB_USART_RX_PDCA_CHANNEL 4
#define LCD_USART_RX_PDCA_CHANNEL 5

#define MY_PDCA					    (&AVR32_PDCA)				//THESE ARE SPI ASSIGNMENTS FOR EVK HACK

#  define EXAMPLE_TARGET_PBACLK_FREQ_HZ FOSC0  // PBA clock target frequency, in Hz

#ifndef USER_BOARD_H
#define USER_BOARD_H

#endif // USER_BOARD_H

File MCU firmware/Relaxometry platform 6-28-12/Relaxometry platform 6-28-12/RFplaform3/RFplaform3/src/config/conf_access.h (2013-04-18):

/*****************************************************************************
 *
 * \file
 *
 * \brief Memory access control configuration file.
 *
 * This file contains the possible external configuration of the memory access
 * control.
 *
 * Copyright (c) 2009 Atmel Corporation. All rights reserved.
 *
 * \asf_license_start
 *
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
 * 3. The name of Atmel may not be used to endorse or promote products derived
 *    from this software without specific prior written permission.
 *
 * 4. This software may only be redistributed and used in connection with an Atmel
 *    AVR product.
 *
 * THIS SOFTWARE IS PROVIDED BY ATMEL "AS IS" AND ANY EXPRESS OR IMPLIED
 * WARRANTIES, INCLUDING, BUT NOT LIMITED TO, THE IMPLIED WARRANTIES OF
 * MERCHANTABILITY, FITNESS FOR A PARTICULAR PURPOSE AND NON-INFRINGEMENT ARE
 * EXPRESSLY AND SPECIFICALLY DISCLAIMED. IN NO EVENT SHALL ATMEL BE LIABLE FOR
 * ANY DIRECT, INDIRECT, INCIDENTAL, SPECIAL, EXEMPLARY, OR CONSEQUENTIAL DAMAGES
 * (INCLUDING, BUT NOT LIMITED TO, PROCUREMENT OF SUBSTITUTE GOODS OR SERVICES;
 * LOSS OF USE, DATA, OR PROFITS; OR BUSINESS INTERRUPTION) HOWEVER CAUSED AND
 * ON ANY THEORY OF LIABILITY, WHETHER IN CONTRACT, STRICT LIABILITY, OR TORT
 * (INCLUDING NEGLIGENCE OR OTHERWISE) ARISING IN ANY WAY OUT OF THE USE OF THIS
 * SOFTWARE, EVEN IF ADVISED OF THE POSSIBILITY OF SUCH DAMAGE.
 *
 * \asf_license_stop
 *
 ******************************************************************************/


 //! Configuration of ctrl_access which is an abstraction layer for memory interfaces (common/services/storage/ctrl_access)

#ifndef _CONF_ACCESS_H_
#define _CONF_ACCESS_H_

#include "compiler.h"
#include "board.h"


/*! \name Activation of Logical Unit Numbers
 */
//! @{
#if VIRTUAL_MEMORY_ENABLE
#define LUN_0                ENABLE   //!< Enable On-Chip Virtual Memory.
#else
#define LUN_0                DISABLE  //!< Disable On-Chip Virtual Memory.
#endif

#if AT45DBX_ENABLE
#define LUN_1                ENABLE   //!< Enable AT45DBX Data Flash.
#else
#define LUN_1                DISABLE  //!< Disable AT45DBX Data Flash.
#endif

#if SD_MMC_SPI_ENABLE
#define LUN_2                ENABLE   //!< Enable SD/MMC Card over SPI or SPI.
#else
#define LUN_2                DISABLE  //!< Disable SD/MMC Card over SPI or SPI.
#endif

#if SD_MMC_MCI_ENABLE
#define LUN_3                ENABLE   //!< Enable SD/MMC Card over MCI or MCI.
#else
#define LUN_3                DISABLE  //!< Disable SD/MMC Card over MCI or MCI.
#endif

#define LUN_4                DISABLE
#define LUN_5                DISABLE
#define LUN_6                DISABLE
#define LUN_7                DISABLE

#if USB_MASS_STORAGE_ENABLE
#define LUN_USB              ENABLE   //!< Enable Host Mass-Storage Memory.
#else
#define LUN_USB              DISABLE  //!< Disable Host Mass-Storage Memory.
#endif

//! @}

/*! \name LUN 0 Definitions
 */
//! @{
#define VIRTUAL_MEM                             LUN_0
#define LUN_ID_VIRTUAL_MEM                      LUN_ID_0
#define LUN_0_INCLUDE                           "virtual_mem.h"
#define Lun_0_test_unit_ready                   virtual_test_unit_ready
#define Lun_0_read_capacity                     virtual_read_capacity
#define Lun_0_wr_protect                        virtual_wr_protect
#define Lun_0_removal                           virtual_removal
#define Lun_0_usb_read_10                       virtual_usb_read_10
#define Lun_0_usb_write_10                      virtual_usb_write_10
#define Lun_0_mem_2_ram                         virtual_mem_2_ram
#define Lun_0_ram_2_mem                         virtual_ram_2_mem
#define LUN_0_NAME                              "\"On-Chip Virtual Memory\""
//! @}

/*! \name LUN 1 Definitions
 */
//! @{
#define AT45DBX_MEM                             LUN_1
#define LUN_ID_AT45DBX_MEM                      LUN_ID_1
#define LUN_1_INCLUDE                           "at45dbx_mem.h"
#define Lun_1_test_unit_ready                   at45dbx_test_unit_ready
#define Lun_1_read_capacity                     at45dbx_read_capacity
#define Lun_1_wr_protect                        at45dbx_wr_protect
#define Lun_1_removal                           at45dbx_removal
#define Lun_1_usb_read_10                       at45dbx_usb_read_10
#define Lun_1_usb_write_10                      at45dbx_usb_write_10
#define Lun_1_mem_2_ram                         at45dbx_df_2_ram
#define Lun_1_ram_2_mem                         at45dbx_ram_2_df
#define LUN_1_NAME                              "\"AT45DBX Data Flash\""
//! @}

/*! \name LUN 2 Definitions
 */
//! @{
#define SD_MMC_SPI_MEM                          LUN_2
#define LUN_ID_SD_MMC_SPI_MEM                   LUN_ID_2
#define LUN_2_INCLUDE                           "sd_mmc_spi_mem.h"
#define Lun_2_test_unit_ready                   sd_mmc_spi_test_unit_ready
#define Lun_2_read_capacity                     sd_mmc_spi_read_capacity
#define Lun_2_wr_protect                        sd_mmc_spi_wr_protect
#define Lun_2_removal                           sd_mmc_spi_removal
#define Lun_2_usb_read_10                       sd_mmc_spi_usb_read_10
#define Lun_2_usb_write_10                      sd_mmc_spi_usb_write_10
#define Lun_2_mem_2_ram                         sd_mmc_spi_mem_2_ram
#define Lun_2_ram_2_mem                         sd_mmc_spi_ram_2_mem
#define LUN_2_NAME                              "\"SD/MMC Card over SPI\""
//! @}

/*! \name LUN 3 Definitions
 */
//! @{
#define SD_MMC_MCI_0_MEM                        LUN_3
#define LUN_ID_SD_MMC_MCI_0_MEM                 LUN_ID_3
#define LUN_3_INCLUDE                           "sd_mmc_mci_mem.h"
#define Lun_3_test_unit_ready                   sd_mmc_mci_test_unit_ready_0
#define Lun_3_read_capacity                     sd_mmc_mci_read_capacity_0
#define Lun_3_wr_protect                        sd_mmc_mci_wr_protect_0
#define Lun_3_removal                           sd_mmc_mci_removal_0
#define Lun_3_usb_read_10                       sd_mmc_mci_usb_read_10_0
#define Lun_3_usb_write_10                      sd_mmc_mci_usb_write_10_0
#define Lun_3_mem_2_ram                         sd_mmc_mci_mem_2_ram_0
#define Lun_3_ram_2_mem                         sd_mmc_mci_ram_2_mem_0
#define LUN_3_NAME                              "\"SD/MMC Card over MCI Slot 0\""
//! @}

/*! \name USB LUNs Definitions
 */
//! @{
#define MEM_USB                                 LUN_USB
#define LUN_ID_MEM_USB                          LUN_ID_USB
#define LUN_USB_INCLUDE                         "host_mem.h"
#define Lun_usb_test_unit_ready(lun)            host_test_unit_ready(lun)
#define Lun_usb_read_capacity(lun, nb_sect)     host_read_capacity(lun, nb_sect)
#define Lun_usb_read_sector_size(lun)           host_read_sector_size(lun)
#define Lun_usb_wr_protect(lun)                 host_wr_protect(lun)
#define Lun_usb_removal()                       host_removal()
#define Lun_usb_mem_2_ram(addr, ram)            host_read_10_ram(addr, ram)
#define Lun_usb_ram_2_mem(addr, ram)            host_write_10_ram(addr, ram)
#define LUN_USB_NAME                            "\"Host Mass-Storage Memory\""
//! @}

/*! \name Actions Associated with Memory Accesses
 *
 * Write here the action to associate with each memory access.
 *
 * \warning Be careful not to waste time in order not to disturb the functions.
 */
//! @{
#define memory_start_read_action(nb_sectors)
#define memory_stop_read_action()
#define memory_start_write_action(nb_sectors)
#define memory_stop_write_action()
//! @}

/*! \name Activation of Interface Features
 */
//! @{
#if ACCESS_USB_ENABLED
#define ACCESS_USB           true  //!< MEM <-> USB interface.
#else
#define ACCESS_USB           false //!< MEM <-> USB interface.
#endif

#if ACCESS_MEM_TO_RAM_ENABLED
#define ACCESS_MEM_TO_RAM    true  //!< MEM <-> RAM interface.
#else
#define ACCESS_MEM_TO_RAM    false //!< MEM <-> RAM interface.
#endif

#define ACCESS_STREAM        false //!< Streaming MEM <-> MEM interface.
#define ACCESS_STREAM_RECORD false //!< Streaming MEM <-> MEM interface in record mode.
#define ACCESS_MEM_TO_MEM    false //!< MEM <-> MEM interface.
#define ACCESS_CODEC         false //!< Codec interface.
//! @}

/*! \name Specific Options for Access Control
 */
//! @{
#define GLOBAL_WR_PROTECT    false //!< Management of a global write protection.
//! @}


#endif  // _CONF_ACCESS_H_

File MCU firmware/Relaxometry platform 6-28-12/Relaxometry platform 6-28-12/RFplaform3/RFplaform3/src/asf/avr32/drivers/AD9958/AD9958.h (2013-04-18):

#define register_write (0)
#define register_read (1<<7)
#define CSR_ADDR 0
#define FR1_ADDR 1
#define FR2_ADDR 2
#define CFR_ADDR 3
#define CFTW0_ADDR 4
#define CPOW0_ADDR 5
#define ACR_ADDR 6
#define LSRR_ADDR 7
#define RDW_ADDR 8
#define FDW_ADDR 9
#define CW1_ADDR 10
#define CW2_ADDR 11
#define CW3_ADDR 12
#define CW4_ADDR 13
#define CW5_ADDR 14
#define CW6_ADDR 15
#define CW7_ADDR 16
#define CW8_ADDR 17
#define CW9_ADDR 18
#define CW10_ADDR 19
#define CW11_ADDR 20
#define CW12_ADDR 21
#define CW13_ADDR 22
#define CW14_ADDR 23
#define CW15_ADDR 24


//CSR register
//[7:6] channel enable registers
#define CH_EN_OFFSET 6
#define CH_EN_0 1
#define CH_EN_1 2
#define CH_EN_BOTH 3
//[2:1] Serial I/O mode
#define SER_MODE_OFFSET 1	//only going to use one of these two modes, not 2 or 4 bit modes...
#define SER_MODE_2WIRE 0
#define SER_MODE_3WIRE 1
//[0] LSB/MSB first
#define LSB_FIRST_OFFSET 0
#define LSB_FIRST	1
#define MSB_FIRST	0
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

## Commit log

2013-04-18 Uploaded boms
    [Control board BOM.xlsx, Misc.xlsx, RF board BOM.xlsx, TPA and Buckmod BOM.xlsx]
2013-04-18 Uploaded Atmel Studio project directory for MCU firmware.
    [TcfTransactionLog.csv]
2013-04-18 Uploaded EAGLE design files
    [CMCD_and_buckmod_FINAL.brd, CMCD_and_buckmod_FINAL.sch, Control board FINAL.brd, Control board FINAL.sch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]
2013-04-18 Fixed minor bug in Toplevel.c Some LCD commands were being sent to USB.
    [TcfTransactionLog.csv]
